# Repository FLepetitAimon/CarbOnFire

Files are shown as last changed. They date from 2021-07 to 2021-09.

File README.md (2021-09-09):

# Système CarbOnFire
***
## Contexte 
Le projet a été réalisé entre juin et aout 2021 au laboratoire d'aérologie de Toulouse, dans le cadre d'un stage de 4é année d'école d'ingénieur. La stage a été fait par François LEPETIT-AIMON et tutoré par Jean-François LEON. Si vous désirez des informations suplémentaires sur le projet, n'hésitez à contacter François LEPETIT-AIMON à l'adresse mail: francois.lepetitaimon@gmail.com

## Présentation du projet

ATTENTION : Avant d’utiliser le système, veillez à lire la fiche technique du projet.

CarbOnFire est un système de mesure d’émission de particules issues de la combustion de végétaux. Il s’inscrit dans un projet d’étude de l’exposition humaine aux particules fines issues de la combustion de biomasse et en particulier aux feux de forêt. Il est affilié au projet FIRECASTER de l’Agence National de la Recherche (ANR). Ce projet a pour but la création d'une plate-forme numérique de simulation des incendies de forêts et des panaches de fumée associées en zone méditerranéenne. Pour évaluer la quantité de fumée émise par un incendie, il est nécessaire de connaître les facteurs d'émission des polluants.  Les facteurs d’émission se définissent comme la masse d'un polluant spécifique émis dans l’atmosphère par kilogramme de végétation brûlée. Pour les évaluer, on mesure les rapports d'émission qui se définissent comme le rapport entre la masse de polluants émises sur celle des concentrations de CO et CO2. 

CarbOnFire est un système qui permet d’analyser la composition de fumées issues de combustions de végétaux. Le système est installé sur un sac à dos pour être facilement transportable.  Il est équipé d’un système de pompage qui aspire les fumées. L’aspiration se fait au bout d’un tuyau que l’utilisateur place au-dessus des feux. Le bout du tuyau est pourvu d’un filtre de quartz dont le rôle est de capter les particules. Après la mesure, le filtre est analysé au laboratoire par des méthodes chimiques, qui permettent de mettre en évidence sa composition. Les fumées filtrées qui arrivent du tuyau, circulent respectivement dans la pompe, le boîtier de mesure et enfin à travers le compteur à gaz. Elles sont ensuite rejetées dans l’air. Le cœur du système réside dans le boîtier de mesure. Il fait l’acquisition des concentrations de monoxyde (CO) et dioxyde de carbone (CO2), de la température et de la pression. Il enregistre les mesures dans une carte SD pour un traitement ultérieur, et transmet en direct, via Bluetooth, les mesures de gaz et de température. Celles-ci peuvent être visualisées sur le terrain avec un smartphone grâce à l’application CarbOnFire.

## Etat de fonctionnement du système

A l'issue des trois mois de développement, le premier prototype du système est en état de marche. Il fait l'acquisition des mesures de CO, CO2, température et pression. Il enregistre les données sur une carte SD et transmet les mesure de CO, CO2 et température vers une application android. L'ensemble du système est intégré sur un sac à dos. Les mesures réalisées en laboratoire et en conditions reélles ont permis de caractériser la qualité des mesures de gaz. Il en ressort qu la précision obtenue est insuffisante et qu'il faut l'améliorer. Le détail des mesures et de leur analyse est décrit dans la fiche technique du Projet.

## Contenu du Github

Le github contient les programmes arduino du projet, les documents techniques, le code de l'application android avec le fichier .apk, les fichiers des mesures réalisées, et enfin les fichiers associés à la conception du PCB.

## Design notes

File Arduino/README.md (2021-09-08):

# Codes Arduino
***

## Environement de Développement 

Pour écrire un programme et le téléverser sur la carte Arduino, vous pouvez utilisez l'IDE foruni par Arduino et téléchargeable gratuitementsur leur site internet (https://www.arduino.cc/en/software). Les codes sont écrit en C++. 

## Progamme Principale

Le fichier ProgrammePrincipale contient le code d'acquisition des mesures. Il effectue des mesures, les enregistre dans un fichier au format .CSV sur une carte SD et transmets trois d'entre elle via une communication bluetooth. Les trois grandeurs concernés sont la concentration de CO, la concentration de CO2 et la température. En complément du programme, il est recommandé d'utiliser l'application android CarbOnFire disponible sur le GitHub dans le répertoire CarbOnFrie_App.

Le montage electrique nécessaire au bon fonctionnement du programme est détaillé dans la fiche technique du projet (répertoire Documents_Techniques). 

## Programme RTC (Real-Time Clock)

Le programme RTC à pour but de régler la RTC. Il se peu qu'avec le temps, la RTC se décale de quelques minutes, ou que la pile soit vide. Dans ce cas, il est nécessaire de régler la RTC. Pour effectuer se réglage suivé les indicationsl suivantes:

1. Ouvrez, avec l'IDE Arduino, le programme test-rtc.ino disponible dans le repertoire Programe_RTC du Github
2. Branchez le shield SD-RTC sur une carte Arduino UNO, et branchez la carte à l'ordinateur. 
3. Téléverser le programme puis ouvrez le port série sur l'IDE
4. Réglez le baudrate du port série à 57600, la listes des commandes devrait s'afficher
5. Commencez par activer la RTC en tapant la commande **c 0 0** 
6. Puis renseignez l'heure actuelle avec la commande **tw yyyymmdd hhmmss dw** avec **dw** qui correspond au jour de la semaine (dim=1, lun=2, ..., sam=7)
7. Vérifiez le bonne mise à jour de l'heure en tapant la commande **tr**, l'heure actuelle doit s'afficher.
8. Reposisitionnez le Shield SD sur dans le boitier de mesure.

## Programme CN0396

Le programme CN0396Exemple sert lire la mesure de CO effectuée par la carte Analog Device CN0396 équpé d'un capteur de CO, CO-CX. La programme offre également la possibilité d'effectuer une correction en température. Le montage électrique est très simple, il suffit de monter la carte Analog Device sur une carte Arduino Uno et de téléverser le programme exemple. Si vous souhaitez utiliser la carte Analog avec un shield Sd, il vous faudra changer le pin CS du bus SPI d'une des deux cartes.

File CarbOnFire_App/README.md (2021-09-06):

# Application CarbOnFire
***
## Fonctionnalités

L'application CarbOnFire accompagne la prsie de mesure du système. Elle permet de visualiser en temps réel les valeurs de CO, de CO2, et de température mesurées par les capteurs. Elle utilise la connexion bluetooth du smartphone sur lequel elle est installée.

## Installation

L'insatllation de l'application se fait par le biais d'un fichier apk. De ce fait il est nécessaire d'avoir un appareil android, l'application ne sera pas instalable sur un appareil apple. Voci la liste des étapes à suivre:

1. Téléchargez sur votre ordinateur le fichier "CarbOnFire.apk" disponible dans le répertoire CarbOnFire_App du github.
2. Branchez votre smatrphone à votre ordinateur.
3. Autoriser le transfert des données par USB dans les paramètres de votre smartphone.
5. Via votre ordinateur, copiez le fichier .apk téléchargé précedement dans les fichiers de votre smartphone. 
6. Sur votre smartphone, lancer le fichier .apk  que vous venez de copier
7. Autoriser l'installation d'application de sources inconnues 
8. L'application devrait s'installer.

## Utilisation

Lorsque vous lancez l’application pour la première fois, il vous est demandé la permission d’accès à la localisation. Cette autorisation est nécessaire pour le fonctionnement du Bluetooth. Il vous faut l’accepter sinon l’application ne fonctionnera pas. Pour se connecter au boîtier, appuyez sur le bouton « DEVICE ». Une liste déroulante s’affiche avec les appareils Bluetooth détectés. Sélectionnez celui correspondant au boîtier. Par défaut, son nom est HMSOFT. Attendez que la connexion se fasse.
Dès que le système de mesure est connecté, les mesures s’affichent et se mettent à jour automatiquement.

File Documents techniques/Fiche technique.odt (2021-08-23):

Fiche Technique

Présentation

CarbOnFire est un système de mesure d’émission de particules issues de la combustion de végétaux. Il a été développé au laboratoire d’aérologie en août 2021. Ce document décrit l’architecture et la conception du système. Si vous désirez des informations supplémentaires sur le projet, n’hésitez pas à contacter François LEPETIT-AIMON à l’adresse électronique francois.lepetitaimon@gmail.com.

ATTENTION : Avant d’utiliser le système, veillez à lire la partie « indication d’utilisation »

Contexte du projet

CarbOnFire s’inscrit dans un projet d’étude de l’exposition humaine aux particules fines, et en particulier, aux émissions issues de feu de cuissons en plein air. Dans beaucoup de pays, la combustion de végétaux est utilisée comme outil de cuisine au quotidien. Le système permettra de calculer les facteurs d’émissions ainsi que les ratios de polluants par CO2 pendant la préparation d’un repas. Il mettra ainsi en évidence la nature de la combustion (complète ou incomplète), et le niveau de nocivité pour la santé du cuisinier. Des études ont déjà été menée et sont toujours menées actuellement. Par exemple en 2019, Aka Jacques Adon avait soutenu sa thèse sur l’impact sur la santé des aérosols issus de source urbaine en côte d’ivoire. Sa thèse est disponible à l’URL suivant : http://thesesups.ups-tlse.fr/4469/.

Caractéristiques techniques du système :

Tension d’alimentation | 12V
Précision mesure de CO | -+ 5ppm
Précision mesure de température | -+1°C
Précision mesure de pression | -+1hPa
Précision mesure de CO2 | -+50ppm
Débit d’air | 10l/min
Capacité carte SD | 32GB
Plage de mesure de température | -10°C à 50°C
Plage de mesure de CO | 0 à 2000ppm
Plage de mesure de CO2 | 0 à 5000ppm
Plage de mesure de pression
Dimensions | 60cm x 30cm x 30cm
Poids | 10Kg
Diamètre de filtre | 45mm

Conception globale du projet

CarbOnFire est un système qui permet d’analyser la composition de fumées issues de combustions de végétaux. Le système est installé sur un sac à dos pour être facilement transportable. Il est équipé d’un système de pompage qui aspire les fumées. L’aspiration se fait au bout d’une perche que l’utilisateur place au-dessus des feux. Le bout de la perche est pourvu d’un filtre de quartz dont le rôle est de capter toutes les particules. Après la mesure, le filtre est analysé au laboratoire par des méthodes chimiques, qui permettent de mettre en évidence sa composition. Les fumées filtrées qui arrivent de la perche circulent respectivement dans la pompe, le boîtier de mesure et enfin à travers le compteur à gaz, elles sont ensuite rejetées dans l’air. Le cœur du système réside dans le boîtier de mesure. Il fait l’acquisition des concentrations de monoxyde et dioxyde de carbone, de la température et de la pression. Il enregistre les mesures dans une carte SD pour un traitement ultérieur, et transmet en direct, via Bluetooth, les mesures de gaz et de température. Celles-ci peuvent être visualisées sur le terrain avec un smartphone grâce à l’application CarbOnFire.

Boîtier de Mesure

Le boîtier de mesure a pour rôle de caractériser quatre grandeurs physiques des fumées aspirées : la concentration de monoxyde de carbone, la concentration de dioxyde de carbone, la température et la pression.

Mesure du Monoxyde de carbone

Pour mesurer le monoxyde de Carbone, nous utilisons un capteur chimique. Le principe de mesure est voisin de celui d’une pile chimique. Le passage du gaz entre deux électrodes provoque une réaction d’oxydo-réduction. Cette réaction produit un courant entre les deux électrodes appelées Working Electrode et Counter Electrode. Dans la gamme de mesure, ce courant est proportionnel à la concentration de CO à laquelle est exposée le capteur. Un capteur chimique est caractérisé par sa sensibilité exprimée en courant par unité de concentration. Plus sa sensibilité est grande plus le courant circulant entre les électrodes sera important à concentration égale. En contrepartie la plage de mesure se restreint quand la sensibilité augmente.

Un des inconvénients de ce type de capteur est les sensibilités croisées. La géométrie du capteur et le choix du matériau des électrodes optimisent la sensibilité du capteur pour le gaz choisi, mais il subsiste des sensibilités non nulles pour d’autres gaz. Il est important de connaître ces gaz pour s’assurer que dans l’application prédestinée, il n’y ait pas de risque de les retrouver.

Pour notre application, nous avons besoin de mesurer des concentrations pouvant atteindre 2000ppm de monoxyde de Carbone. Nous avons choisi d’utiliser le capteur alphasense CO-CX dont la plage de mesure est 0-2000ppm. Sa sensibilité est comprise entre 55 et 100nA par ppm d’après le constructeur, ce qui représente un grand intervalle d’incertitude. Afin de réduire cette incertitude, il est nécessaire que le capteur soit étalonné avant son utilisation. Voici les principales caractéristiques assurées par le constructeur :

On peut retenir sur la qualité de la mesure que la réponse admet un bruit RMS de +-0,5ppm, que la mesure du 0 peut-être biaisée de -+3ppm et enfin que l’erreur de linéarité engendre au maximum une déviation de 40ppm par rapport à la valeur vraie.

Les principales sensibilités croisées sont les suivantes :

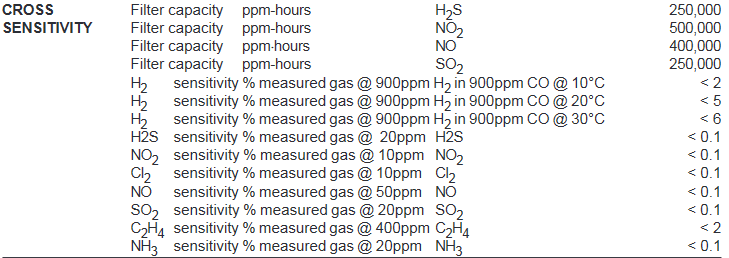
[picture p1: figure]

Il est important de noter que les performances du capteur sont impactées par la température. Plus la température est différente de 20°C, plus l’erreur de linéarité est grande et plus la dérive du zéro est importante. Voici les résultats de dérive en température fournis par le constructeur :

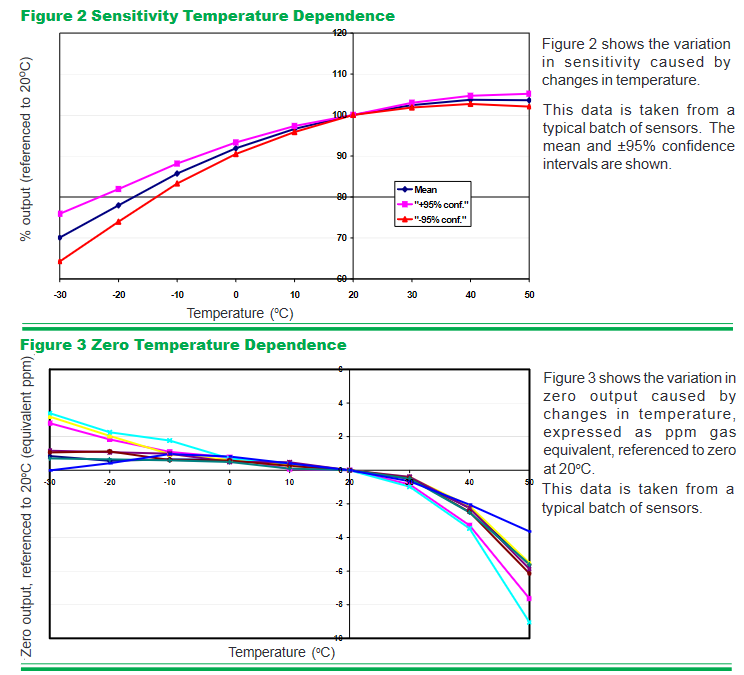
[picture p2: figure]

Pour pouvoir traiter la mesure, il faut amplifier le faible courant de réponse en un courant plus grand mesurable. Pour cela on utilise la carte électronique alphasense « 4 to 20 mA Digital Transmitter Board » qui est conçue spécialement pour le CO-CX. Elle amplifie le signal du capteur en un courant variant de 4mA à 20mA. Cette amplification se fait grâce à un circuit potentiostatique dont voici le schéma du montage :

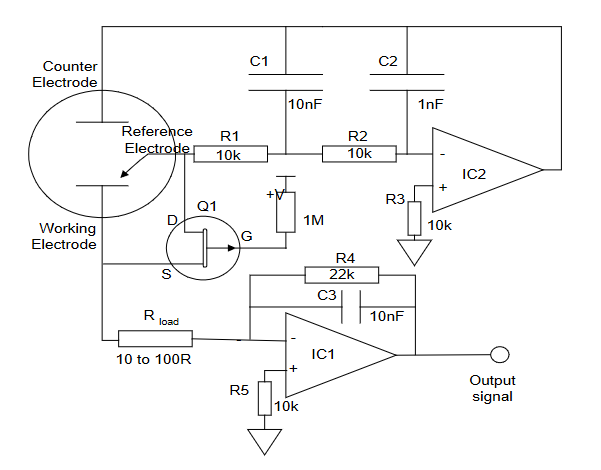
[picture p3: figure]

On peut noter que le capteur possède une 3ème électrode « Reference Electrode ». Cette électrode sert à appliquer une tension d’offset entre elle et la « Working Electrode ». La valeur de cette tension dépend du capteur utilisé, pour le capteur CO-CX, elle doit être nulle.

La sortie de la carte électronique alphasense est un courant variant de 4mA à 20mA. Ce courant de sortie est numérique avec une résolution de 0.75µA. Rapporté à l’entrée cela correspond à une résolution de 11nA. On sait que la sensibilité du capteur est comprise entre 55 et 100 nA/ppm et que son bruit RMS est de l’ordre de 0.5ppm. En termes de courant, ce bruit vaut entre 27nA et 50nA. La résolution de la carte est inférieure à ce bruit, donc elle ne sera pas limitante.

En sortie, la précision de la carte est de -+5µA, a laquelle il faut ajouter le bruit RMS pouvant aller jusqu’à 2 µA. Rapporté à l’entrée l’incertitude sur la mesure est d’environ 100nA. Cette incertitude est limitante car elle est supérieure au bruit du capteur. En termes de concentration, cela correspond à une incertitude de -+1 à 2ppm. Il faut encore ajouter à cette erreur la dérive en température qui est importante : -+0.2uA/°C en sortie. On arrive à -+4ppm de précision à 25°C, soit 10 fois moins précis que la précision potentielle du capteur seul.

La carte est alimentée en 10-30V par un connecteur molex KK2,54 de 2 pins. La valeur du courant en sortie de la carte est convertie en tension en ajoutant une résistance en série entre l’alimentation et le capteur :

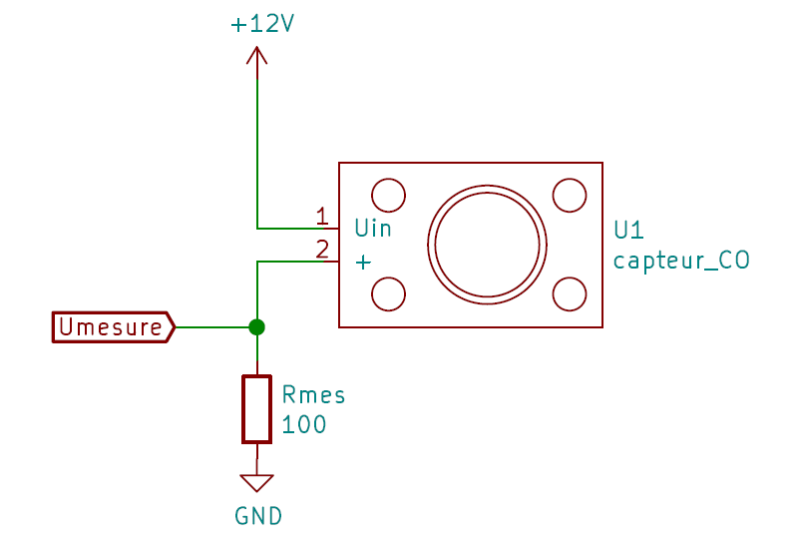
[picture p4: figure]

En utilisant la loi d’ohm on obtient les plages de tensions de mesures suivantes :

U0ppm = 0,004Rmes ; U1000ppm = 0,020Rmes.

La résistance de mesure induit une chute de tension aux bornes du capteur par rapport à la tension d’alimentation. La valeur maximale de cette chute de tension est de 0,020R. Malgré cette chute, la tension aux bornes du capteur ne doit pas être inférieure à 10 volts. La chute de tension doit donc être inférieure à une tension seuil :

dUseuil= Ualimentation – 10V

Dans notre cas, la tension d’alimentation vaut 12V, donc la chute de tension doit être inférieure à 2V. En terme résistif, la résistance de mesure doit être inférieure à une résistance seuil :

Rseuil = dUseuil/Imax = 2/0,02 = 100Ohms.

Nous avons choisi Rmes = Rseuil = 100Ohms pour maximiser la plage de tensions de mesures et ainsi optimiser la résolution numérique de l’adc.

N.B : Si vous souhaitez obtenir d’avantage d’informations sur le capteur et sa carte électronique alphansense, les datasheets et les notices d’utilisations sont disponibles en annexe.

Test et étalonnage

Nous avons mesuré la réponse du système pour deux concentrations de CO connues, une concentration de 0ppm et une concentration de 92ppm. Les mesures ont été réalisées pendant une période de forte chaleur, la température à l’intérieur du boitier a atteint 40°C. Cette température peut impacter à -+5ppm les résultats présentés.

Pour la concentration de 0ppm, la concentration initiale dans l’air ambiant de la salle de mesure est de 15ppm. L’air injecté dans le boitier a une concentration en CO de 1bpm, bien inférieure au bruit du capteur -+0.5ppm. Voici les résultats obtenus pour un débit d’air de 1l/min :

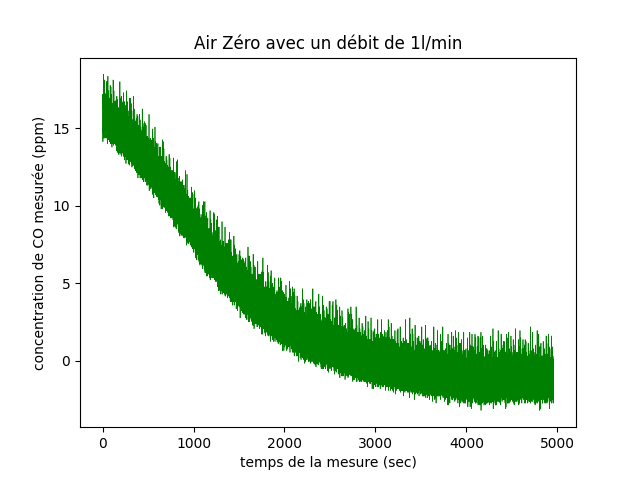
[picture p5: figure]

La mesure du zéro se stabilise légèrement en-dessous de 0ppm, à environ -2ppm. Cela peut venir de plusieurs paramètres : la dérive en température ou le mauvais étalonnage du capteur. On peut remarquer que le bruit de mesure est de -+3ppm. Cela correspond aux spécifications attendues qui sont de -+3ppm.

Le temps de réponse du capteur est très long, on doit attendre entre 30 minutes et 1 heure pour obtenir un zéro stable. Le constructeur ne s’est pas avancé sur le temps de réponse à 0ppm, mais ce temps de réponse est du même ordre de grandeur que celui du capteur de CO2. La géométrie du système et en particulier à l’écartement du capteur par rapport au flux d’air peut également augmenter le temps de réponse.

La deuxième concentration étudiée est le 92ppm. La concentration initiale dans le boitier est de -2ppm. L’air est injecté dans le boitier avec un débit de 9.7l/min. Voici les résultats obtenus :

La précision de la mesure est du même ordre de grandeur que pour le 0ppm, à savoir -+ 5ppm. Le temps de réponse est de 50 secondes alors que le constructeur annonçait un temps de réponse de 40 secondes pour une variation de 0ppm à 400ppm. Nous sommes au-dessus de ce temps de réponse, les hypothèses sur les raisons de ces écarts sont les mêmes que pour le 0ppm, à savoir l’éloignement du capteur par rapport au flux d’air.

En résumé, la précision des résultats obtenues correspond à la précision attendue compte tenu des caractéristiques du capteur et de la carte de traitement du signal. La mesure est précise à -+5ppm avec un bruit de mesure de -+5ppm. Le temps de réponse est plus important mais reste dans l’ordre de grandeur annoncé par le constructeur.

Alternatives

La carte électronique Alphasense limite la sensibilité du capteur. Elle admet un bruit de mesure bien supérieur au bruit généré par le capteur chimique. D’autres alternatives existent, par exemple la carte EVAL-CN0396-ARDZ développée par Analog Device, semble avoir une réponse plus stable.

Voici la comparaison des réponses des deux cartes de mesures équipées du même capteur CO-CX:

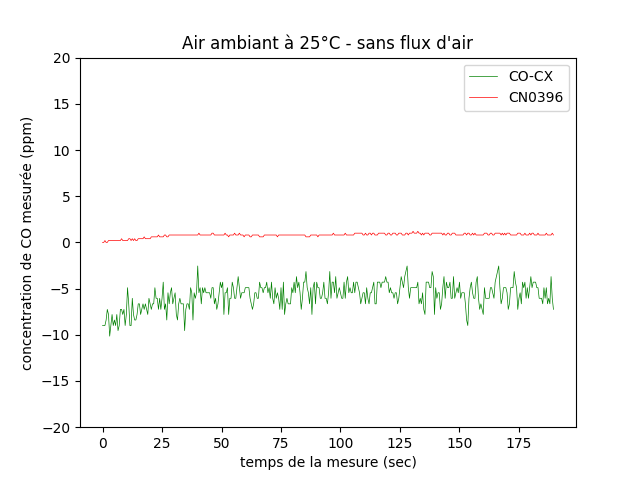
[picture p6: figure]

On voit clairement que la carte CN0396 fournie une réponse beaucoup plus stable (-+0.05ppm). Pour conclure sur la précision de la carte, il faudrait effectuer des tests à concentration connues comme présentés précédemment. Malgré tout, on peut faire l’hypothèse que la concentration de CO en intérieure est très proche de 0ppm. Dans le cadre de cette hypothèse, la précision de la carte Analog Device semble très bonne (-+0.2ppm).

En revanche en termes d’intégration dans un système de mesure, la carte CN0396 est plus contraignante. Elle s’utilise uniquement avec une carte arduino uno. Elle est montée en shield, ce qui oblige à prendre un boitier suffisamment haut et limite les choix de placement du capteur. Une possibilité serait d’imprimé un PCB personnalisé avec le circuit électrique de la carte CN0396. Voici le schéma électrique :

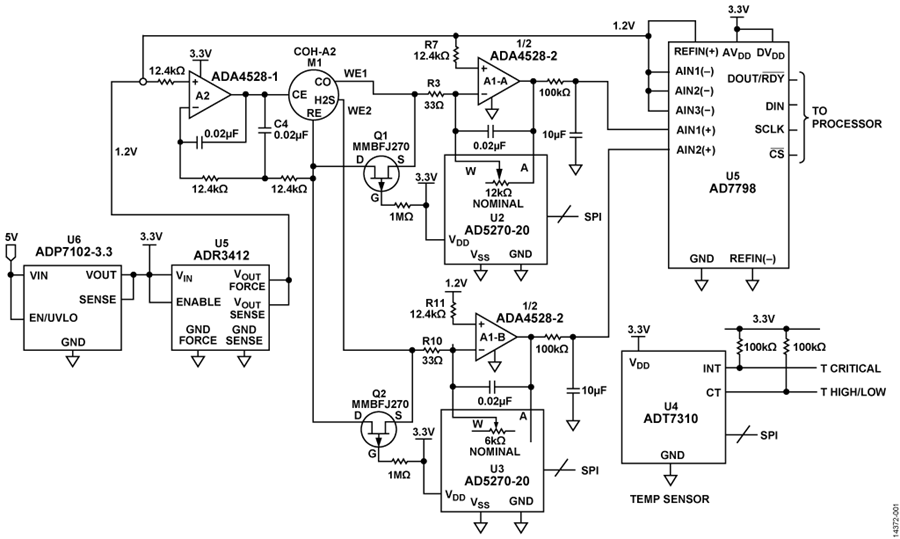
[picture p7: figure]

Mesure du Dioxyde de Carbone

La mesure de monoxyde de Carbone est assurée par un capteur infra-rouge NDIR Alphasense. Voici le principe de fonctionnement. Une LED infra-rouge envoie des pulses de courant à travers une cavité, qui communique avec l’air ambiant. Deux photodétecteurs sont installés à l’intérieur de la cavité face à la photodiode. Le premier est dit actif et le second est dit de référence. Ils mesurent l’intensité lumineuse transmise à travers la cavité. Le photodétecteur actif est équipé d’un filtre qui transmet uniquement la longueur d’onde d’une raie d’absorption du CO2, (lambda = 4µm). De cette manière lorsque la concentration en CO2 augmente dans la cavité, l’intensité lumineuse transmise diminue. L’autre photodétecteur est équipé d’un filtre qui absorbe uniquement la longueur d’onde de la raie d’absorption. De cette manière l’intensité lumineuse transmise n’est pas impactée par la variation de concentration de CO2. La cavité de référence sert à compenser les variations d’intensité d’émission lumineuse.

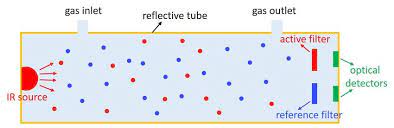
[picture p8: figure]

La concentration de CO2 dans l’air ambiant est fonction de la différence des mesures d’intensité lumineuse entre les deux détecteurs. Les photodétecteurs sont sensibles aux variations de température, c’est la raison pour laquelle ils sont accompagnés d’une thermistance permettant d’établir une correction de compensation thermique sur la mesure.

Pour notre application nous utilisons le capteur Alphasense IRC-A1 de type IAQ dont la plage de mesure est 0-5000ppm. Sa résolution est de -+1ppm à 0ppm et peut atteindre -+15ppm à 5000ppm. La précision du capteur est de -+50ppm (en utilisant les coefficients universels de linéarisation, annexe AAN401-05). Le temps de réponse du capteur est inférieur à 40 secondes d’après le constructeur. En revanche pour atteindre le zéro les temps de réponse sont plus long. Il faut 30 secondes pour atteindre le 0 à -+100ppm et il faut 30 minutes pour atteindre un zéro qui respect les spécifications constructeurs à savoir -+1ppm.

Voici les performances générales du capteur :

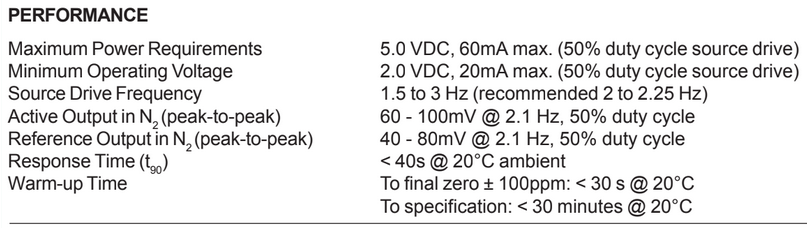
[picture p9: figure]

Voici le descriptif des broches du capteur indiqué dans la datasheet :

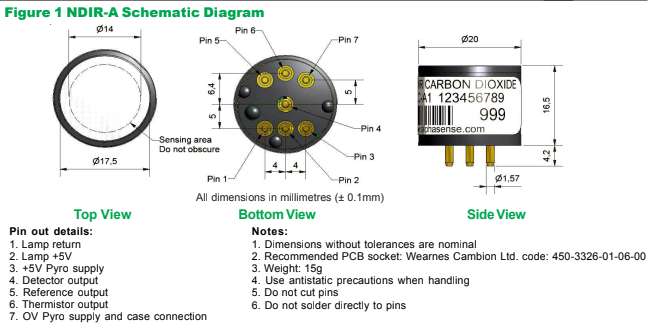
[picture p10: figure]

Le signal d’alimentation de la source lumineuse doit être un signal carré de 2 à 2,5Hz de fréquence, de rapport cyclique 50 % et d’amplitude 5V. La source de tension doit avoir une impédance de sortie d’environ 9 à 10Ohms et doit pouvoir fournir un courant de 50 à 60mA. Pour créer ce signal, on peut utiliser un transistor MOSFET à canal n couplé à un signal carré sur la grille (voir figure 2 pour le branchement). Cependant il faut bien s’assurer que le GND du transistor et le GND des photodétecteurs soit isolés pour éviter toutes perturbations de la mesure.

Les signaux bruts issus des photodétecteurs sont composés d’un offset d’environ 0,7 à 1V et d’une composante alternative de fréquence identique à la fréquence d’alimentation de la source lumineuse. Cette oscillation a une amplitude de 20mV à 50mV peak-to-peak qui varie en fonction de la transmission lumineuse à l’intérieur de la cavité. Pour traiter le signal il faut filtrer la composante continue ainsi que les hautes fréquences puis amplifié le signal :

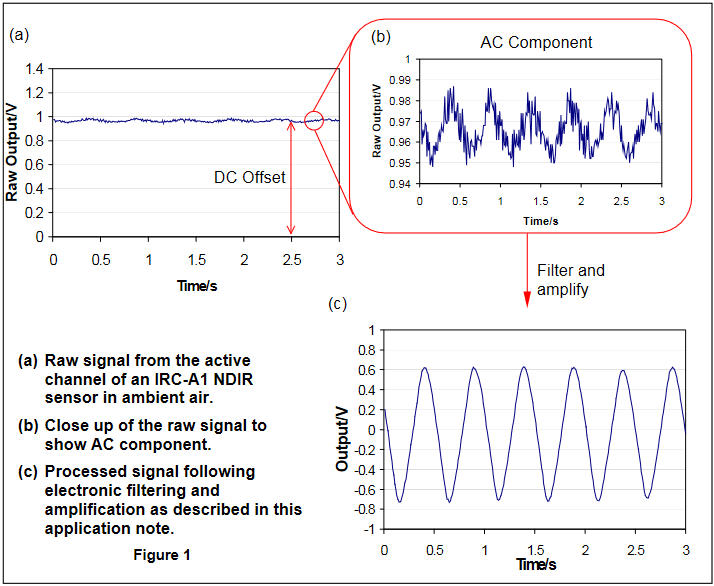
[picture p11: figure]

On obtient un signal sinusoïdal pour chacune des deux photodiodes, dont l’amplitude traduit le taux de transmission des rayons issus de la LED infra-rouge à travers la cavité.

Voici un schéma électrique qui permet de faire clignoter la source lumineuse et amplifier le signal des photodétecteurs :

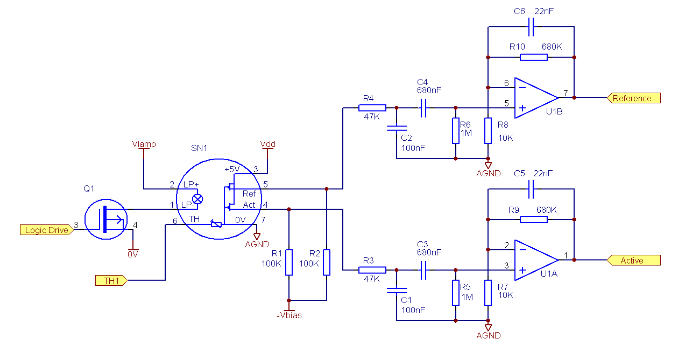
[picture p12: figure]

L’annexe AAN 202-04 détail la conception du circuit.

La thermistance à coefficient de température négatif (NTC), servant à mesurer la température, vaut 3000Ohms à 25°C et son coefficient B vaut 3450 K. On peut évaluer la valeur de la résistance en fonction de la température grâce à la relation de Steinhart-Hart simplifiée valable sur la plage de température de fonctionnent du capteur :

R(T)= R0 * exp(B*(1/T - 1/T0))

avec T0 = 25°C et R0 = 3000Ohms

En travaillant l’équation on obtient la valeur de la température en fonction de la résistance mesure :

T = T0*B/(T0*ln(R(T)/R0)+B)

Dans le capteur, la thermistance est connectée entre les broches 6 et 7. Pour effectuer la mesure de résistance, il faut connecter la broche 6 du capteur en série avec une résistance de valeur connue, et une source de tension également connue. En utilisant le principe du pont diviseur de tension, on peut connaître la valeur de la thermistance et donc mesurer la température :

Ainsi R(T) = (Vcc/Umes)*R1 – R1

Les détails des calculs de concentration de CO2 et de compensation thermique sont disponibles en annexe (document AAN 201-06).

Dans notre cas nous avons utilisé la carte alphasense IRC-TX spécialement conçue pour le capteur IRC-A1. Elle renvoie un signal en courant variant de 4mA à 20mA. La précision de la mesure est la même que celle du capteur, à savoir -+50ppm.

La carte est alimentée en 12-30V par les pins 1 et 2 du connecteur molex KK2,54 4-pins. Le principe de l’acquisition est le même que pour le capteur de CO. Un courant proportionnel à la concentration de CO2 allant de 4mA à 20mA circule entre le pin 3 et le pin 4 du connecteur molex. Une résistance de mesure est intégrée en série entre les pins 3 et 4 pour convertir la réponse en courant en une réponse en tension. La tension maximale mesurable par notre système d’acquisition est de 5V. D’après la loi d’Ohm, une tension maximale de 5V pour un courant maximal de 20mA est obtenue pour une résistance Rmesure = Umax/Imax = 250Ohms. La valeur standard la plus proche est 220Ohms, c’est celle que nous utilisons.

En résumé, on obtient en entrée de notre système d’acquisition une tension proportionnelle à la concentration de CO2 variant de Umin = 0.004R = 0,88V à Umax = 0.020R = 4,4V, sur la plage de mesure 0-5000ppm.

Voici le branchement électrique de la carte IRC-TX :

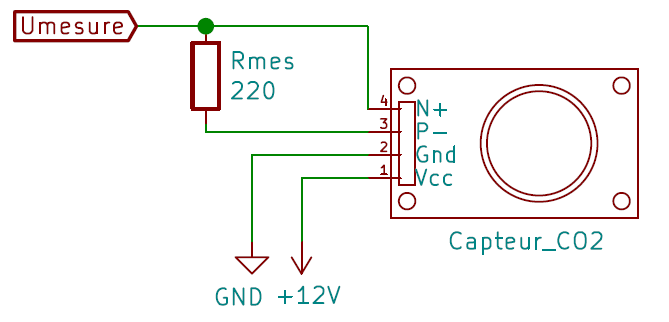
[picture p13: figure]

Tests et résultats

Comme pour le capteur de CO, nous avons étudiés la réponse la carte IRC-TX couplée avec le capteur IRC-A1 pour deux concentrations de CO2 : 0ppm et 1000ppm.

Pour le 0ppm, nous utilisons une bombonne qui fixe le CO2 de l’air ambiant. La concentration ainsi obtenue, est en toute vraisemblance inférieure à 1ppm, mais nous n’avions pas d’appareils de mesure permettant de le vérifier au moment de l’expérience. Nous en ferons donc l’hypothèse. Voici les mesures observées :

On peut observer que la mesure se stabilise à 0ppm -+10ppm. Le temps de mesure est d’environ 40 minutes. Le constructeur assurait une précision de -+50ppm et un temps de réponse de 30minutes. La précision mesurée est en accord avec les spécifications du constructeur, en revanche le temps de réponse est un peu plus long. Ce délai est sans doute dû à la géométrie du système, comme nous en avons discuté pour le capteur de CO.

La mesure de 1000ppm est faite avec une bouteille pressurisée de concentration 998ppm -+0,1 %. Elle est branchée directement sur le boîtier, le débit est réglé à 10 l/min. Voici la courbe obtenue :

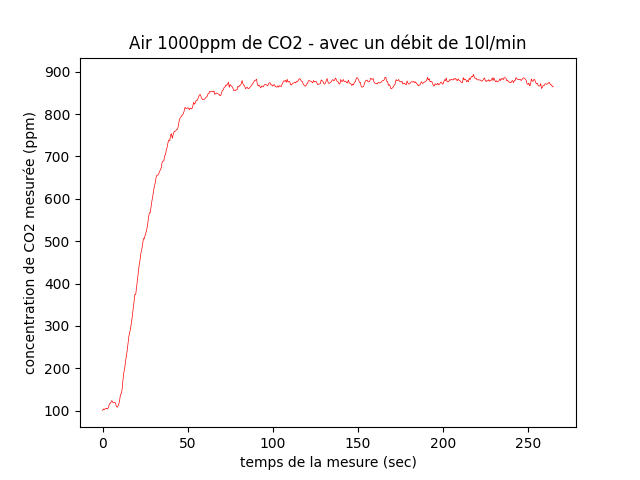
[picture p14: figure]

On peut observer que la valeur de stabilisation est de 900 ppm -+10ppm soit un écart de 100ppm par rapport à la concentration réelle. Cet écart est en dehors des marges du constructeur, et n’est pas acceptable. Il faudrait effectuer un étalonnage du capteur pour corriger cette imprécision. Le document d’assistance à l’étalonnage des capteurs, est fourni par alphasense et est disponible en annexe.

Le temps de réponse est d’environ 40 secondes. Il est légèrement supérieur aux 30 secondes prédites par le constructeur. Une fois encore cet écart peut être dû à la géométrie du système. Dans le cadre de l’application ce temps de réponse est acceptable, c’est la raison pour laquelle nous n’avons pas mis en œuvre des solutions pour le réduire.

Mesure de température et de pression.

Les mesures de température et de pression sont obtenues avec le capteur BMP280. C’est un capteur qui communique via le bus i2c. Il mesure la température ambiante avec une précision de 1°C et la pression ambiante avec une précision de 1hPa. À partir de la mesure de pression atmosphérique, le BMP280 peut calculer l’altitude à 1 mètre prêt. Cette précision est atteinte à la condition de renseigner quotidiennement la pression courante à l’altitude 0, qui varie en fonction des conditions météorologiques.

L’alimentation du capteur se fait par les pins 1 et 2 du connecteur Grove. Les mesures sont communiquées par les canaux SCL et SDA du bus i2c (pin 3 et 4 du connecteur Grove).

Système d’acquisition des mesures de gaz.

L’acquisition des mesures est assurée par l’Arduino Uno rev3 assisté d’un ADC 16-bits adafruit. Nous avons fait le choix d’ajouter un ADC extérieur en raison des mauvais résultats obtenus en utilisant l’ADC de l’Arduino. En termes de résolution théorique, l’ADC 10-bits de l’Arduino aurait suffi pour obtenir une précision de 6ppm sur la mesure de CO et de CO2. Cependant en comparant les résultats obtenus avec l’Arduino et avec l’ADC Adafruit, on observe une nette différence de mesure, supérieure à la résolution théorique mesure (-60ppm par rapport à l’adc de l’arduino). Malgré sa résolution suffisante, l’Arduino n’a pas la précision nécessaire. L’ADC utilisé est un ADS1115 Adafruit 16-bits. Il peut accueillir 4 canaux analogiques et communique en i2c en utilisant la librairie ‘Adafruit_ADS1X15.h’.

Ainsi toutes les acquisitions de mesures (température, pression, concentrations de gaz) se font avec les canaux i2c de l’Arduino.

Enregistrement des mesures et RTC.

La carte arduino est accompagnée d’un shield SD de TRU COMPONENT muni d’une Real Time Clock (RTC) (Ref : TC-8579880). Il équipé d’un lecteur de carte SD et d’une RTC DS1307ZN. La RTC est alimentée par une pile bouton de type CR1220, qui permet de garder en mémoire la date et l’heure, quand le système est éteint.

Communication Bluetooth

CarbOnFire est équipé d’un module Bluetooth qui communique par bus série v.3. Le module est branché avec un connecteur Grove dont les pins correspondent dans l’ordre au tx, rx, Vcc, Gnd. Les pins digitaux 0 et 1 de l’arduino sont par default dédiés à la communication série, le branchement du module est donc très simple :

Panneau Face avant

Sur la face avant du boîtier, on retrouve les éléments de contrôle d’alimentation :

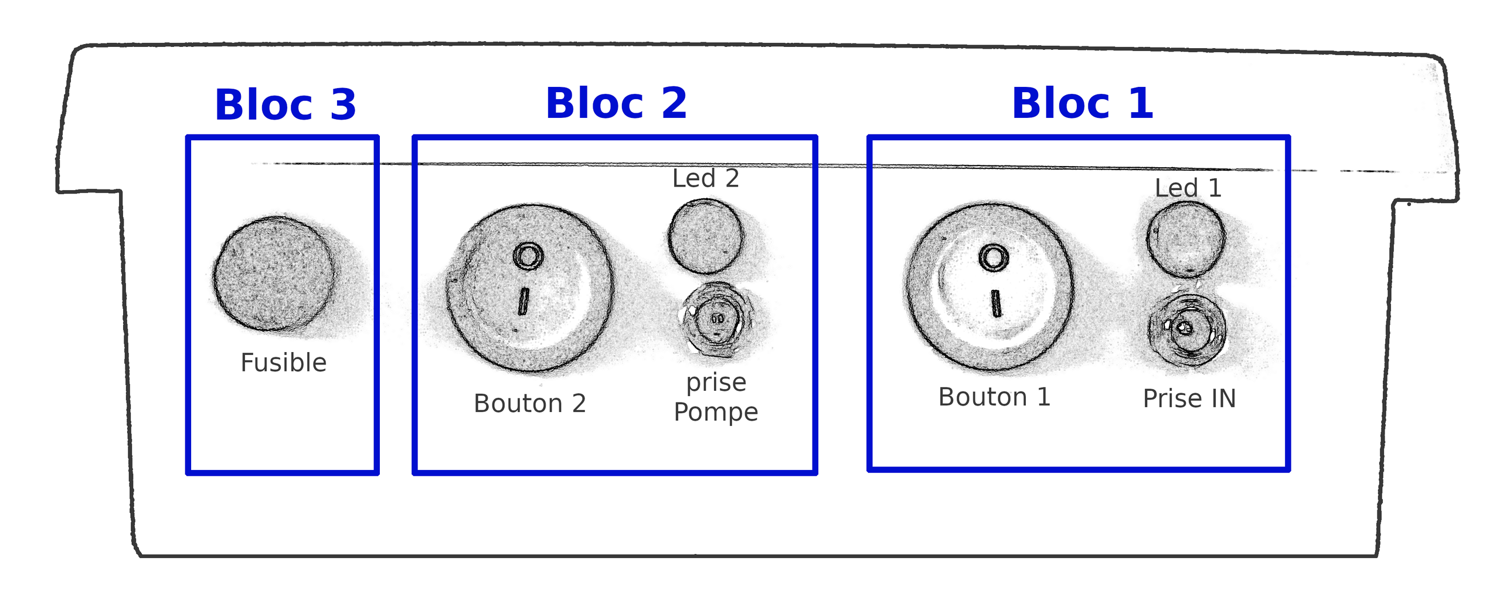
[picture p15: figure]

Le bloc 1 sert à alimenter le système de mesure. Il est constitué d’un bouton ON/OFF, d’une prise d’alimentation CC 12Volt et d’un voyant vert. Le voyant s’allume lorsque le système de mesure est en marche.

Le bloc 2 sert à alimenter la pompe. Il est constitué des mêmes éléments que le bloc 1, à savoir un bouton, un voyant et une prise CC. Il est important de noter que la prise CC du bloc 2 est une sortie d’alimentation contrairement à celle du bloc 1 qui est une entrée. Elle est connectée aux bornes de la pompe avec un câble CC vers double cosses.

Le bloc 3 est constitué d’un porte-fusible qui protège le système de mesure d’une éventuelle surcharge. Il accueille un fusible de 500mA changeable facilement depuis l’extérieur.

Isolation de l’alimentation de la pompe

Pour assurer une bonne précision dans les mesures, l’alimentation des capteurs doit être stable. La batterie fournie une tension très stable, mais dans la mesure où la pompe est branchée en parallèle du système de mesure, elle peut induire un bruit dans la tension d’alimentation. Pour éviter ce bruit, nous avons ajouté deux éléments. Le premier est une diode de roue libre. Elle empêche la propagation d’un courant inverse dû à l’inertie du rotor lors de l’arrêt de la pompe. Le deuxième est un condensateur de filtrage de 1uF, qui filtre les variations de tensions à haute et moyenne fréquence dû à la rotation du moteur.

Organisation des éléments dans le boîtier et assemblage mécanique

Le boîtier est organisé en deux parties délimitées par une cloison en PVC horizontale. La partie inférieure est un SAS dans lequel circule le flux d’air. Les capteurs de gaz et le BMP280 sont situés dans ce SAS pour baigner dans l’air extérieur. Les deux embouts du conduit d’air sont placés face à face, et les capteurs de gaz sont légèrement décalés par rapport au flux d’air.

La partie supérieure du boîtier accueille le montage électrique. On y retrouve les cartes des capteurs, le Shield SD monté sur la carte Arduino Uno, le module Bluetooth, l’ADC, le bornier, les connections du panneau de face avant, ainsi que tous les câbles de connexions entre chacun des ces éléments.

Les boutons de contrôle sont encastrés dans la paroi du boîtier, tandis ce que les voyants, les prises d’alimentation et le porte-fusible sont serrés à la paroi avec un écrou. Les deux embouts traversent-cloisons d’entrée et de sortie d’air, sont également serrés sur la paroi avec un écrou. Le reste des composants sont fixés sur la cloison de séparation par un système de vis écrous.

Étanchéité du boîtier

Les jonctions du panneau de face avant et des embouts traversent-cloisons sont susceptibles de générer des fuites. Pour éviter ce problème, ces zones sont étanchéifiées par le dépôt de silicone liquide. En séchant elle durcit et forme un couche souple et étanche. Le couvercle du boîtier est équipé d’un joint, qui assure l’étanchéité quand le boîtier est fermé.

Impact du débit sur les mesures

Une des options pour améliorer le temps de réponse des mesures de gaz, est de placer les capteurs dans le flux d’air. Si cette option est appliquée, il faut prendre en compte l’impact de la vitesse du flux d’air sur les mesures. En effet il semblerai que la vitesse du flux d’air ait une forte influence sur la mesure de CO2 et une légère influence sur la mesure de CO.

Pour effectuer cette observation, nous avons fait une série de mesure dans l’air ambiant avec la pompe éteinte et avec la pompe allumée. Voici les résultats obtenus :

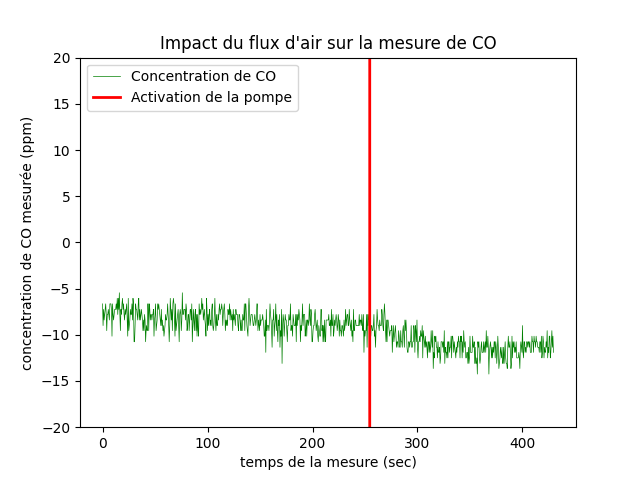
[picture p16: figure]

On observe que la mesure de CO décroît de 5ppm lorsque la pompe se met en route, alors que la mesure de CO2 augmente de 50ppm. Pour le CO ces variations semblent acceptables. Il faudrait vérifier que le phénomène ne s’amplifie pas pour des concentrations de CO plus élevée.

La variation de la mesure de CO2 est à la limite de l’acceptable, il faudrait étudier ce phénomène de manière plus rigoureuse de manière à corriger la dérive de la mesure.

Batterie

Le système est alimenté en 12V avec une batterie de Plomb rechargeable de 7 A.h. Les batteries utilisées sont de la marque Radio Spare, réf : 537-5488. Chaque système est équipé d’une unique batterie qui alimente la pompe et le boîtier de mesure. L’autonomie du système est d’environ 7heures.

Une autre solution serait d’alimenter la pompe avec une autre batterie pour réduire l’impact de l’alimentation de la pompe sur l’alimentation du système de mesure.

Programme Arduino

Comme tous les programmes arduino, le script se décompose en deux parties : une partie setup() qui s’exécute une unique fois à la mise sous tension, et une partie loop() qui tourne en boucle. Voici les étapes qu’exécute le programme :

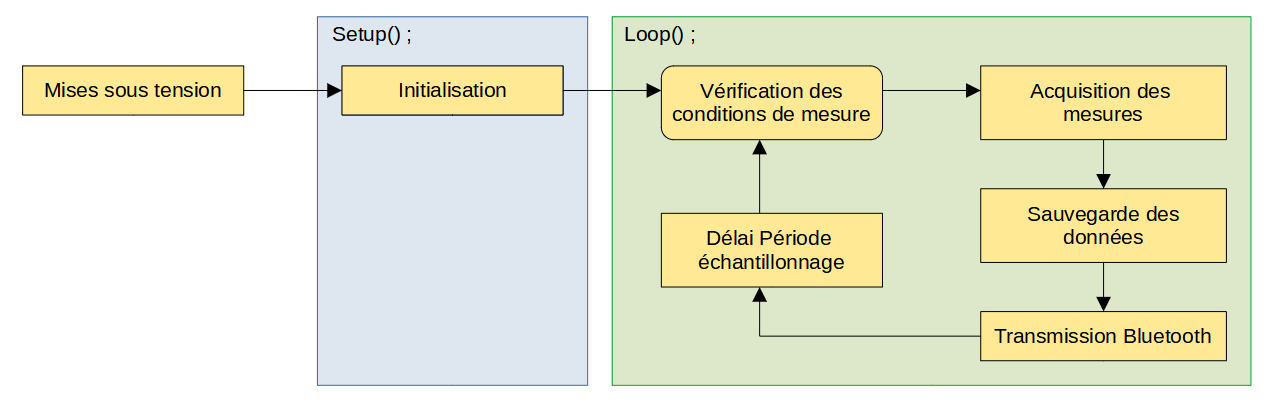
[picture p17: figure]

Initialisation

Dans le setup(), nous préparons les composants électriques pour qu’ils soient opérationnels. De manière générale chaque composant à une librairie dédiée dans laquelle figure une fonction d’initialisation intitulée classiquement begin(). Elle permet de vérifier que la communication se fait entre la carte et le composant (branchement, temps de réponse, …) et parfois de définir des paramètres (ex : baudrate pour le Serial). Dans notre cas il y a 4 éléments à initialiser : le bmp280, le shield SD, l’adc 16-bits et le port série du module Bluetooth.

Plus loin dans le programme, les données sont écrites dans un fichier sur la carte SD. C’est un fichier au format csv (Coma Separate Values), avec une première ligne d’entête correspondant aux intitulés des colonnes de mesure :

Si le fichier de mesure sur la carte a été supprimé, où s’il n’a jamais été créé, il faut le créer et y écrire la première ligne d’entête. Cela se fait dans la partie Setup(). Un répertoire « donnée » est d’abord créé, puis un fichier DATA y est ajouté avec la première ligne d’entête. A l’inverse, si le fichier existe déjà et qu’il contient des mesures, il ne faut ni les effacer, ni ajouter une ligne d’entête en plein milieu. Les nouvelles mesures seront ajoutées à la suite de celles déjà écrites.

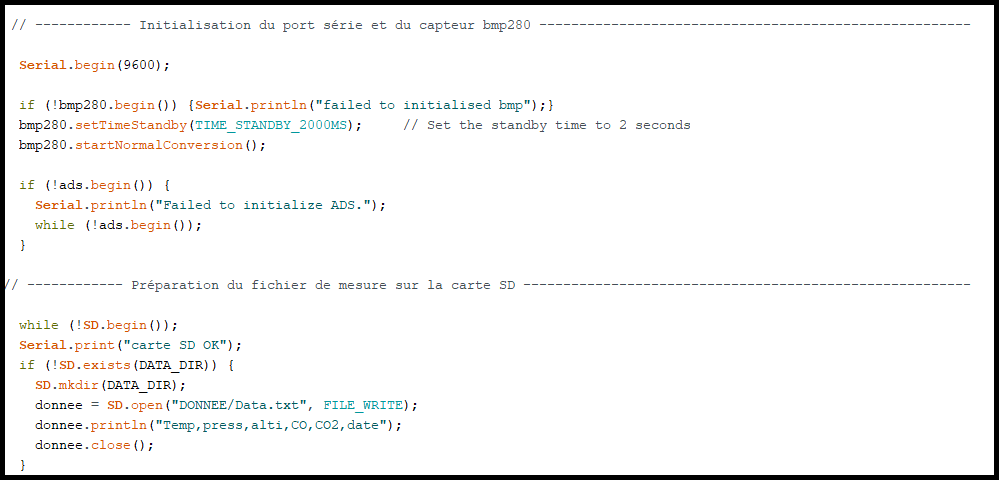
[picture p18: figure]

Vérification des conditions de mesures

Une fois l’initialisation faite, nous entrons dans la boucle du programme. C’est dans cette boucle que s’effectue les mesures et leur gestion, notamment leur sauvegarde. Avant de démarrer une acquisition, il faut vérifier que nous sommes en capacité d’enregistrer la mesure. Autrement dit, il faut s’assurer qu’il y ait une carte SD dans le lecteur et que la communication avec le Shield SD puisse s’établir. Le programme contient une boucle bloquante qui attend qu’une carte SD soit insérée dans le lecteur.

Acquisition des mesures

L’acquisition des mesures de CO et CO2 se fait grâce à l’adc 16-bits qui communique en I2C. La fonction readADC_singleEnded(Pin) renvoie une valeur numérique entre 0 et 655536. Celle-ci est proportionnelle à la tension mesurée sur le broche numérotée « Pin ». La valeur 0 correspond à une tension de -Vsat et la valeur 655536 correspond à une de tension de +Vsat. L’ADC possède un gain réglable allant de x2/3 (par défaut) jusqu’à x16. La tension Vsat dépend de ce gain :

GAIN | Vsat | Résolution
x 2/3 | 6.144 V | 0.1875 mV
x 1 | 4.096 V | 0.125 mV
x 2 | 2.048 V | 0.0625 mV
x 4 | 1.024 V | 0.03125 mV
x 8 | 0.512 V | 0.015625 mV
x 16 | 0.256 V | 0.0078125 mV

Pour convertir la valeur binaire en une tension de mesure, on utilise la fonction computVolts(valeur_binaire). Elle renvoie la tension en tenant compte du GAIN sélectionné.

Le programme Arduino contient deux fonctions, ConcentrationCO() et ConcentrationCO2(), qui renvoient respectivement la mesure de concentration de CO et de CO2. Elles utilisent le principe de mesure décrit plus haut dans les parties « mesure de CO2 » et « mesure de CO ». Dans un premier temps, la tension mesurée par l’adc aux bornes des résistances de mesure est convertie en courant par loi d’ohms.

Imes = Umes/Rmes

Sachant qu’un courant de mesure de 4mA équivaut à une concentration de 0ppm et qu’un courant de mesure de 20mA équivaut à une concentration de 5000ppm, on déduit la relation suivante :

Cmes = (Imes – I0ppm) * (5000ppm/I5000ppm)

Au final on a:

Cmes = ((Umes/Rmes) – I0ppm) * (5000ppm/I5000ppm)

Les mesures de CO, CO2, température, pression et altitude ainsi que la date sont enregistrées temporairement dans un tableau de float intitulé Tab_Mesure[]

Sauvegarde sur la carte SD

La nouvelle série de données disponible dans le tableau de mesure est ajoutée au fichier de mesure sur la carte SD par l’appelle de la fonction EcritureCarteSD(). Les données sont écrites selon les règles de syntaxe du format CSV : les mesures sont séparées par des virgules, et chaque série de mesure se finit par un retour à la ligne.

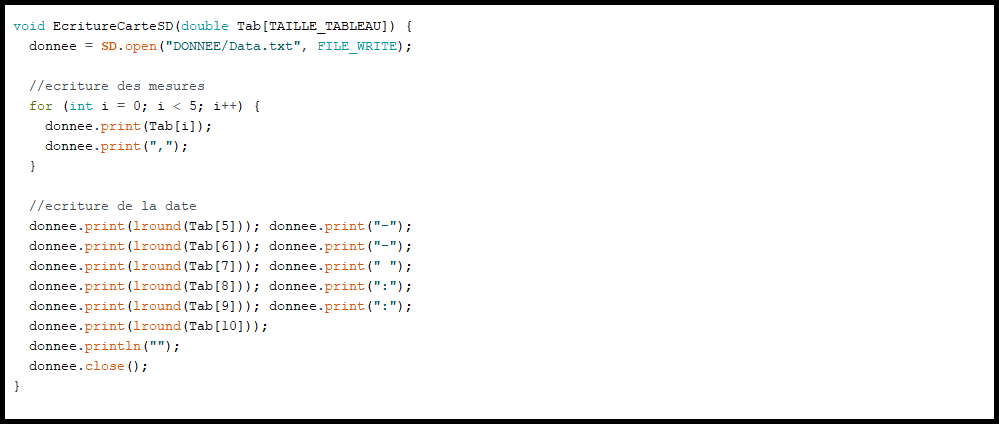
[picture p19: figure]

Transmission Bluetooth

La transmission Bluetooth se fait grâce au module Bluetooth qui utilise le port série (pin rx et tx). Uniquement trois données sont transmises par Bluetooth, à savoir la température, la concentration de CO et la concentration de CO2. Elles sont envoyées dans une trame de caractères dont la syntaxe est bien définie : chaque série de mesure se fini par une virgule et dans une même série, chaque mesure est séparée par un point-virgule.

Délai période d’échantillonnage

En fin de boucle, est placée une temporisation de T secondes, avec T la période d’échantillonnage souhaitée. Elle est fixée à 1 secondes. Il est possible de la diminuer, mais dans la mesure ou les changements de concentrations se font de manière progressive et lente (de l’ordre de quelques secondes), et sachant que le temps de réponse des capteurs est de 30 secondes, nous n’avons pas trouvé nécessaire de prendre plus de mesures.

Application Android

Fonctionnement de l’application

L’application Android permet de visualiser en direct les mesures de CO, CO2 et de température mesurées par le boîtier. Au lancement de l’application, nous observons l’interface d’accueil dont la partie supérieure permet de gérer l’état de connexion avec le système, tandis ce que la partie inférieure permet d’afficher les mesures.

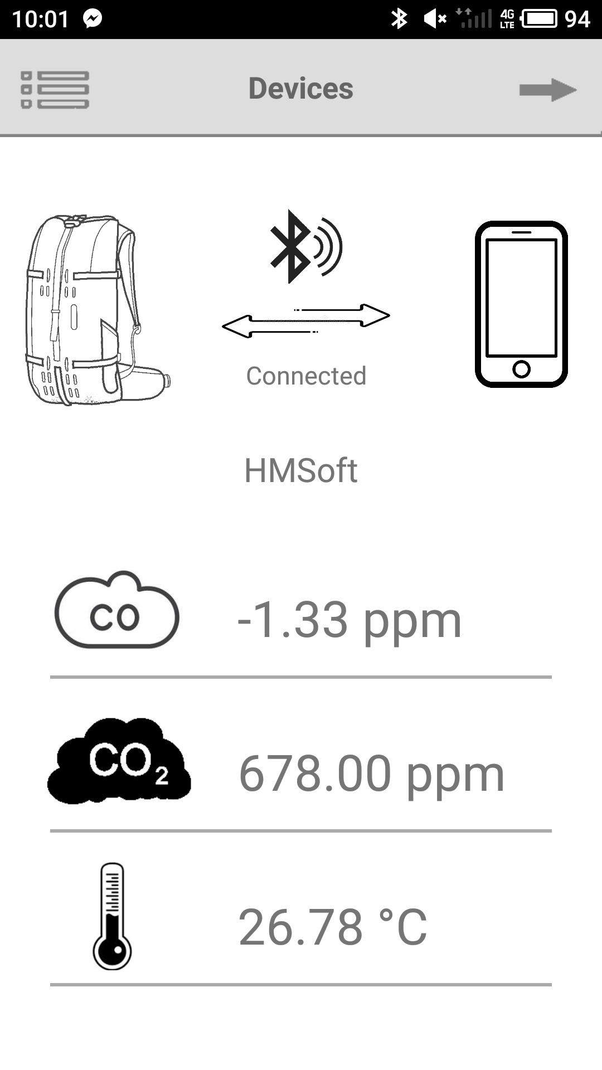
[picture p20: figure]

Lors de la première mise en route du système, l’application demande l’accès à la localisation. Cette autorisation est nécessaire à la communication Bluetooth entre le smartphone et le CarbOnFire.

Au démarrage de l’application aucun appareil n’est connecté. Il faut appuyer sur le bouton « DEVICE ». Une liste déroulante s’affiche alors, au fur et à mesure que de nouveaux appareils disponibles sont découverts.

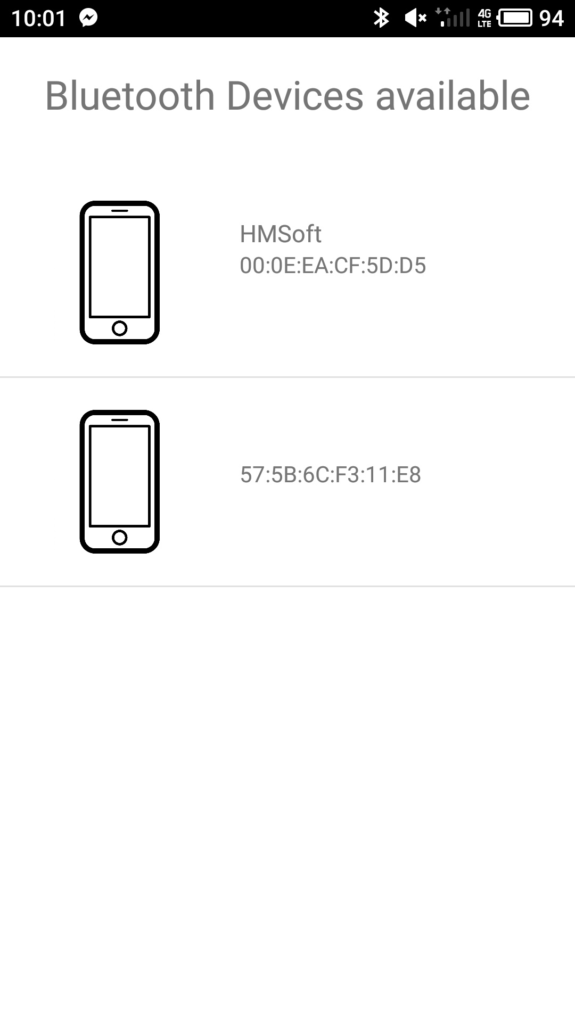
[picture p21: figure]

Lorsque l’utilisateur sélectionne un appareil, l’application tente de s’y connecter. L’utilisateur est notifié de cette tentative par un logo animé de chargement. À la fin du chargement, le nouvel état de connexion est affiché sur l’écran.

Si la connexion est établie, les mesures s’affichent et sont rafraîchies dès qu’une nouvelle trame est reçue.

Si le système de mesure se déconnecte, l’application notifie se changement d’état dans un délai de 8 secondes.

Vision globale de l’organisation du code JAVA

Si vous n’êtes pas familier avec le codage d’application Android, les concepts et objets utilisés sont expliqués dans les grandes lignes. Si vous souhaitez en savoir plus, des liens vers le site Android Devellopeur sont renseignés en note de bas de page.

L’application est composée de deux activités et de deux threads. Les threads et les activités sont deux types de classes Java. En d’autres termes, ce sont deux types de code Java qui ont des rôles bien définis et différents. Dans le cadre du projet, les activités sont les piliers de l’application. Elles ont pour rôle principal de gérer les interactions entre l’utilisateur, l’interface graphique et la logique de l’application. Ce sont en quelques sorte les chefs d’orchestre de l’application. Les threads quant à eux, contiennent du code qui s’exécute en parallèle des activités. Ils n’interagissent pas avec l’interface graphique et permettent de faire tourner un code annexe en parallèle de l’exécution de l’activité courante. Ils sont souvent utilisés pour exécuter des fonctions bloquantes en arrière-plan sans que l’interface graphique ne soit figée.

Le fait d’appartenir à une classe, permet de définir une fois pour toute des fonctions partagées par plusieurs codes de même nature. Prenons l’exemple de la classe activité. Dans la classe Activité, des fonctions sont déjà implémentées pour faciliter le codage de l’activité. On retrouve entre autres, des fonctions dites callback qui exécute un code, écrit par le développeur, à la suite d’un événement particulier. Par exemple la fonction onCreate() exécute un code, au lancement de l’activité.

Dans notre application, la première activité, MainActivity, gère l’interface principale qui est l’interface d’accueil où sont affichés l’état de connexion et ainsi que les dernières mesures reçues. La deuxième activité, ActivityDevice, gère l’interface de choix d’un appareil Bluetooth.

Pour ce qui est des threads, l’un d’eux, appelé ConnectThread, sert à effectuer une tentative de connexion avec un appareil Bluetooth. L’autre, MyBluetoothService, sert à assurer la communication Bluetooth avec un appareil connecté. Il reçoit les trames de mesures et les envoie à l’activité principale.

Scénario général de l’application

Au démarrage de l’application, la code de la MainActivity s’éxécute et l’utilisateur voit s’afficher l’écran d’accueil. Lorsque l’utilisateur appuie sur le bouton « DEVICE », il lance une nouvelle activité, l’activité ActivityDevice. Le lancement de la nouvelle activité s’accompagne d’un changement d’interface graphique. L’écran de choix d’appareil bluetooth est affiché. L’activityDevice débute dès son lancement par scanner les appareils Bluetooth visibles, et les affiche sur la liste au fur et à mesure de leur découverte. L’utilisateur peut sélectionner un appareil de la liste. Lorsqu’il le fait, l’ActivityDevice mémorise l’appareil sélectionné et le transmet à l’activité principale. L’activityDevice est alors arrêtée et l’utilisateur revient dans l’activité principale sur l’écran d’accueil.

Si l’utilisateur à choisi un appareil, l’activityMain démarre une tentative de connexion avec cet appareil. Elle utilise pour cela un thread ConnectThread. Le thread communique avec la MainActivity par le biais d’un objet Handler qui a le rôle de messager. Il permet l’échange d’informations entre les deux entités. En attendant des nouvelles du ConnectThread, l’ActivityMain continue de tourner normalement. Si un message informant le succès de la connexion avec l’appareil souhaité est reçu par l’activité, le ConnectThread est arrêté, et un nouveau thread, MyBluetoothDevice est lancé. Ce thread reçoit les séries de caractères envoyées par l’appareil Bluetooth couramment connecté. Il les transmet à la MainActivity dans des messages envoyés via le Handler. Ces séries de caractères sont recomposées par la MainActivity puis décodées pour en extraire les valeurs des mesures et les afficher.

Si la communication Bluetooth est interrompue, le trhead MyBluetoothService informe la MainActivity qui arrête le thread MyBluetoothService et notifie l’utilisateur.

Indication d’utilisation

Assemblage

Comme nous l’avons évoqué au début, le système est composé de quatre éléments installés sur le sac à dos : la batterie, la pompe, le compteur à gaz et le boîtier de mesure. Le sac à dos comporte deux étages. Sur le premier étage est placée la pompe, vissée sur la plaque, et la batterie, maintenue par un élastique. Sur le deuxième étage est fixé le compteur à gaz. La fixation du boîtier de mesure n’est pas encore défini. Pour les tests il est scotché sous la plaque du deuxième étage.

Une fois que tous les éléments sont fixés, on peut brancher le circuit d’air. Le long tuyau équipé du porte-filtre à une extrémité, est branché par l’autre extrémité sur l’entrée de la pompe.

La sortie de la pompe est branchée par un petit tuyau au connecteur gauche du boîtier de mesure.

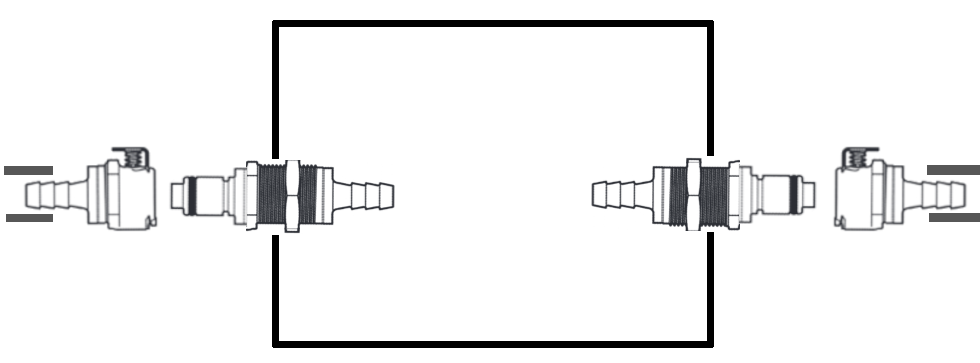
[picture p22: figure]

Enfin le connecteur droit du boîtier est branché à l’entrée du compteur à gaz.

Mise en route du système

Avant de mettre en route le système, il faut vérifier qu’il est bien branché. Un câble doit partir de la batterie et arriver sur le prise d’entrée d’alimentation du boîtier. C’est un câble cosse vers prise CC.

Photo branchement alimentation boitier

Ensuite il faut brancher la pompe à la prise de sortie du boitier. Pour cela on utilise le câble cosse mal vers prise CC.

Photo branchement alimentation pompe

A ce stade, si vous actionnez le bouton ON/OFF du système de mesure, la led verte devrais s’allumer. Cela signifie que le système de mesure est actif. Si vous appuyez sur le bouton ON/OFF de de la prise d’alimentation de la pompe, la pompe devrais s’allumer. Si ce n’est pas le cas, laisser le bouton sur ON et actionnez l’interrupteur situé directement sur le câble de la pompe. A noter que la led verte prévu pour la pompe n’est pas branchée car ses pattes de connexion sont cassées, elle sera donc toujours éteinte.

Connexion avec l’application

Pour visualiser les mesures vous pouvez télécharger l’application CarbOnFire. Pour cela, rendez-vous sur le github à l’URL : le ReadMe de l’application contient toutes les instructions d’installations.

Lorsque vous lancer l’application pour la première fois, il vous ait demandés la permission d’accès à la localisation. Cette autorisation est nécessaire pour le fonctionnement du bluetooth. Il vous faut l’accepter sinon l’application ne marchera pas. Pour se connecter au boîtier, appuyer sur le bouton « DEVICE ». Une liste déroulante s’affiche avec les appareils Bluetooth détectés. Sélectionnez celui correspondant au boîtier. Par défaut, son nom est HMSOFT. Attendez que la connexion se fasse.

Dès que le système de mesure est connecté, les mesures s’affichent et se mettent à jour automatiquement.

Récupération des données

Pour récupérer les données après une mesure, il faut retirer la carte SD. Pour cela il faut commencer par extraire le boitier du sac à dos, puis dévisser les quatre vis de fixation du couvercle. Enlevez le couvercle et la carte SD est directement accessible sur le shieldSD.

Réglage de la RTC

Il est possible que la RTC se dérègle (plus de pile, dérive de l’heure avec le temps), il faut alors la remettre à l’heure. Pour ce réglage il faut branché à un PC le shield SD monté sur une carte arduino uno. Il y a plusieurs options, soit vous branchez directement le carte arduino uno du boitier sans rien démonter, soit vous extrayez uniquement le shield SD du boitier et le monté sur une autre carte arduino uno extérieur au boitier. Il vous faut ensuite lancer le programme de calibration de la rtc disponible sur le github. Lisez le ReadMe associé pour plus de détail.

Si vous utiliser la carte arduino du boîtier pour régler l’adc, n’oubliez pas de retéléverser le programme principale sur la carte, une fois le réglage terminé.

Problème pouvant être rencontrés

Le boitier n’est pas visible en Bluetooth : Ouvrez le boîtier et vérifier l’état de la led jaune du module bluetooth.

Photo led jaune module bluetooth

Si elle clignote, le problème vient du smartphone. Essayer de redémarrer l’application puis si ça ne fonctionne pas, redémarrez votre téléphone.

Si elle reste allumée, cela veut dire qu’un autre appareil Bluetooth est connecté au module. Vous pouvez essayer d’éteindre le boitier et le rallumer pour réinitialiser le bluetooth.

Si elle est éteinte, cela veut dire qu’il y un problème dans le branchement. Vérifiez que les câbles soient bien branchés.

Le boîtier est connecté en Bluetooth mais les mesures ne s’affichent pas : Cela veut dire qu’il y a un problème dans l’initialisation du programme.

- vérifiez que la carte SD est bien présente.

- vérifiez que l’adc et le BMP280 sont bien branchés (pour le détail des branchement voir partie circuit electrique dans construction du boitier de mesure).

Construction du boîtier de mesure

Avant de construire le système veillez à lire tout lire, et en particulier la dernière partie sur les conseil de construction.

Perçage du boîtier

Le boitier est percé en face avant pour accueillir les éléments du panneau avant : boutons, LED, prises et porte-fusible. Voici le schéma avec les cotations :

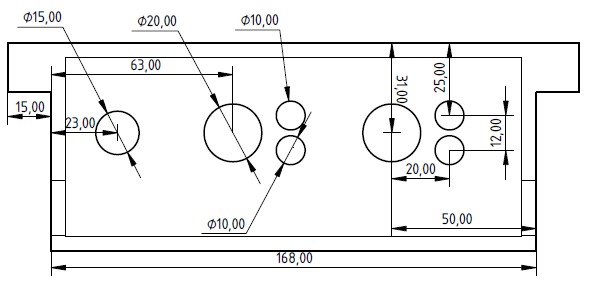
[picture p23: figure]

Le boitier est aussi percé sur les cotés pour accueillir les connexions rapides pour les tuyaux. Voici les cotations :

Le boîtier est percé au fond pour fixé les supports :

Enfin, il faut glisser le joint fourni avec le boitier dans la rainure du couvercle.

Cloison horizontale

La cloison horizontale est fabriquée à partir d’une grande plaque de PVC épaisse de 3mm. Voici les cotation de perçage :

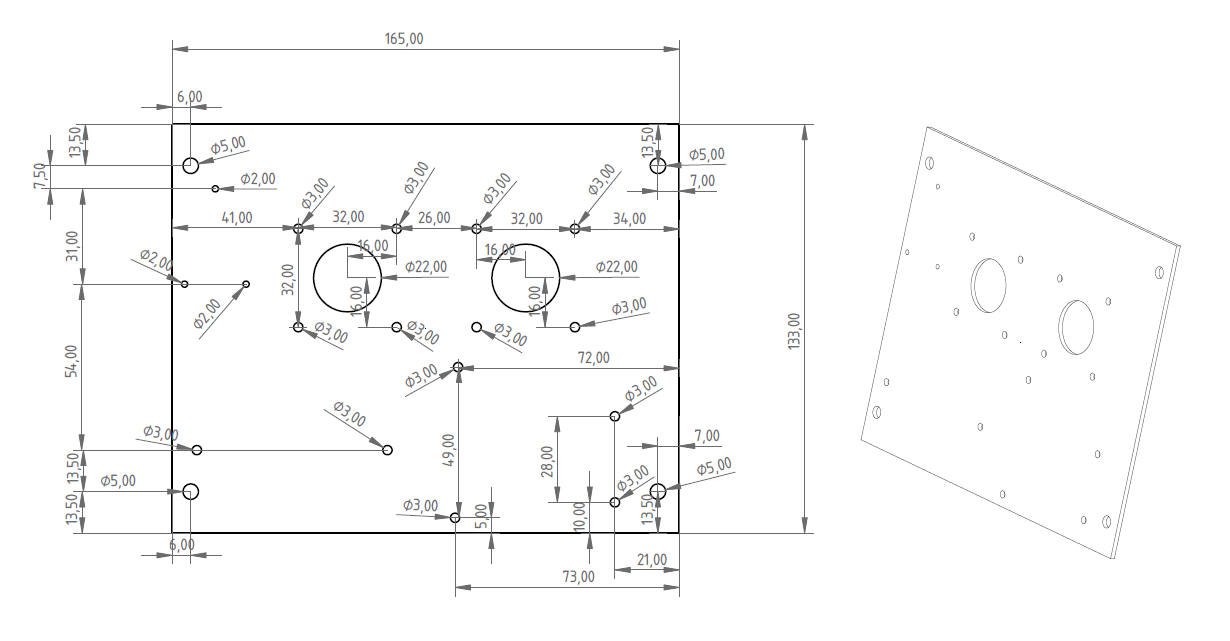
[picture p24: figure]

Support cloison

La cloison est supportée par deux piliers longitudinale. Les piliers sont fixés par des vis M3 avec le fond du boîtier et par des vis M5 avec la cloison. Voici les cotations :

Les trous des vis sont filetés. Pour réaliser ces trous, il faut percer le pilier avec les cotations présentes sur le schéma. Puis il faut tarauder le trou avec des tarauds M3 ou M5 en fonction du trou.

Panneau avant

Les éléments du panneau avant sont insérer dans leurs trous respectifs puis fixés par deux méthodes différentes. Les boutons sont uniquement clipsés, tandis ce que les autres éléments sont serrés sur la paroi par un système de vis-écrous. Voici la disposition des éléments

Circuit électrique

Shield SD

Le shield SD contient une zone libre pour faire des soudures. Pour le système 2 port groves y sont soudés. Le premier permet la connexion i2C avec les capteurs tandis ce que l’autre permet la connexion UART avec le module bluetooth. Le pas de la plaquette de soudure du shield est de 2,54mm alors que le pas du connecteur grove n’est que de 1,2mm. Pour cette raison il est nécessaire de plier légèrement les pattes du connecteur pour les insérer dans la plaquette de soudure.

Les deux connecteur sont placé l’un en face de l’autre comme montré sur la photo. Les connexions avec les pins de la carte arduino sont effectué sur la face arrière Voici le scéhma du montage :

Image soudure shield SD

PCB adc

Les circuits électriques extérieurs aux différentes cartes sont installés sur un PCB conçu spécialement pour le projet. Il est composé d’un bornier de 14 fils, de deux port grove i2c, d’une fiche de connexion pour l’adc adafruit, de deux connecteur molex pour le capteur de CO et celui de CO2, et une prise CC d’alimentation 12V pour la carte arduino.

photo PCB

Le bornier sert à connecter les 7 dipôles du panneau de mesure. Les deux connecteurs grove i2c sont connectés ensemble. L’un deux sert à connecter le BMP280, l’autre sert à connecter l’ensemble du bus i2c à la carte arduino. Le connecteur molex 4-pin est utlisé pour connecter le capteur de CO2. Le circuit de mesure présenté dans la partie mesure de CO2 est imprimé sur le PCB. Le connecteur molex 2-pin est utilisé pour connecter le capteur chimique de CO. Le circuit de mesure présenté dans la partie mesure de CO est également imprimé sur le PCB.

L’adc adafruit vient se brancher dans la fiche de connexion prévue pour. Le PCB contient le circuit électrique permettant d’une part de connecter l’adc au bus i2c et d’autre part de connecter les voies 0 et 1 aux tensions de mesure des capteurs de CO et CO2.

Voici le schéma électrique, le masque du PCB ainsi que le schéma de soudure :

circuit électrique, schéma de soudure, masque PCB

Câbles de connexion

Pour assurer les connexions entre les éléments, 3 types de câbles sont utilisés. Les câbles présents entre le panneau avant et le bornier de connexion du PCB sont des câbles à plusieurs brins, coupés sur mesure. Les câbles grove sont des câbles de taille standard pré-assemblé. Les câbles molex sont des câbles à sertir. Ils doivent être assemblé avant de pouvoir être utilisé. Ils sont composé de 3 pièce détachées : les fils, les boîtiers de connecteurs et les contacts à sertir. Il faut dans un premier temps sertir les contact sur les fils, puis engager les contacter dans les boîtiers de connecteurs :

Schéma contact à sertir

Câblage des éléments électriques

Une fois que tous les éléments sont prêts, il faut les brancher. Le mieux est de commencer par le panneau avant. Les câble du panneau avant sont soudés sur les broches de connexion de chacun des éléments du panneau. Les autres extrémités des fils sont insérer dans leur emplacements respectifs dans le bornier puis visser. La taille de chaque câble est ajusté sur mesure pour limiter le volume de câble dans le boîtier. Voici le schéma de connexion du bornier :

schéma de connexion du bornier

Les deux bornes des boutons et du porte-fusible sont équivalentes, il n’y a pas d’ordre de connexion. En revanche pour les led et les prise d’alimentation, il faut repérer la nature des bornes. Pour les led, une inversion des bornes n’impactera pas le système, mais la led ne s’allumera pas. Pour les prises d’alimentation, un inversion des bornes peut endommager le système. Voici le descriptif des broches des prises d’alimentation :

schéma borne prise CC

Une fois que le bornier est connecté au panneau de face avant, il faut connecter les capteurs. Les deux câbles molex, doivent être connecté chacun sur leur capteur respectif. Un cable grove i2x est branché entre le capteur de BMP280 et un des port i2c du PCB. L’autre cable grove i2c est connecté entre le deuxième port i2c du PCB et le port i2c soudés sur le shield SD. Le connecteut CC du PCB est connecté au port jack de l’arduino. L’adc est encastré dans les fiches de connexion qui lui sont dédiées. Enfin le connecteur grove UART du module Bluetooth est branché sur le port UART soudé sur le shield SD.

Photo branchement final

Assemblage du boîtier

Les composants électrique sont fixés sur la cloison par un système de vis écrou. Ils sont tous fixés sur la face supérieur de la cloison à exception du BMP280 qui est fixé sous la cloison. Le BMP280 et le module Bluetooth sont fixés de part et d’autre de la cloison par les trois mêmes vis.

La cloison est fixée sur ses piliers par 4 vis M5 en polyester.

Schéma de fixation cloison – piliers

Les piliers sont fixés au boîtier par 4 vis M3 :

schéma fixation boîtier - piliers

Conseil d’ordre de construction

Pour la construction du boîtier, il est nécessaire de commencer par la fabrication séparées des éléments mécaniques et électriques, à savoir le perçage du boîtier, la fabrication de la cloison et ses support, l’impression du PCB et le soudage des connecteurs grove sur le shield SD. Ensuite, il est conseillé de suivra l’ordre d’assemblage suivant :

1 - fixez les piliers avec le boîtier, en mettant sous le pilier, et surtout au niveau des deux trous, une couche de silicone pour assurer l’étanchéité de la fixation.

2 - fixez des embouts PLC traverse cloison sur le boitier. Avant de serrer l’écrou, appliquer une couche de silicone en bordure du trou pour assurer l’étanchéité.

3 - installez les éléments du panneau avant et mettre une couche de silicone pour assurer l’étanchéité.

4 - soudez les fils de connexion sur les broche du panneau avant en prévoyant large pour la taille du fil.

5 - fixez les éléments électriques sur la cloison horizontale.

6 - branchez le module bluetooth au shield SD.

7 - fixez la cloison sur les piliers

8 - branchez les fils du panneau avant en les faisant passer derrière le module bluetooth. Ajustez la taille de chaque fil pour qu’il soit juste assez long pour atteindre son emplacement dans le bornier.

9 - branchez les autres cables.

10 - placez le joint dans la reinure du couvercle. Apliquer un point de sylicone à la jonction des deux bouts de joints.

11 – Fermez le boîtier avec les 4 vis cruciforme.

Remarques et Perspectives

Annexe

datasheet capteur et carte d’acquisition

liste des pièces et référence

bibliographie

thèse

github

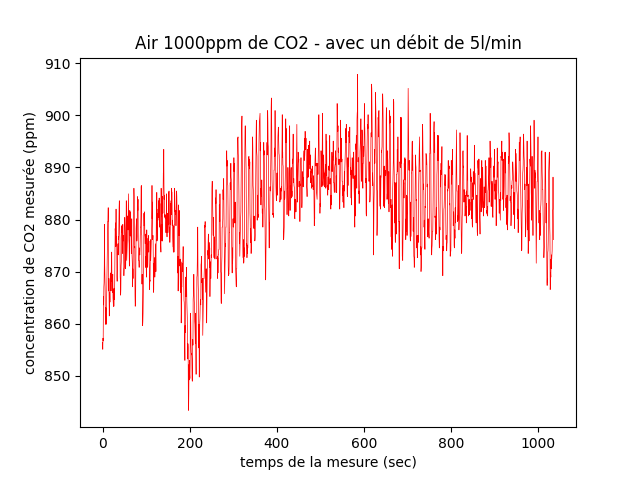
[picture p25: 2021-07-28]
Mesures/Etalonnage_22-07-21/courbes/figure_de_CO2_1000ppm_5lmin.png

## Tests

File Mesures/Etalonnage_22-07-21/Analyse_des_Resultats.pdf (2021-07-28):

# R´esultats d’´etalonnage du 22/07/21

Capteurs de CO et CO2

## 1 Montage de l’exp´erience

Pour r´ealiser l’´etalonnage des capteurs, nous avons utilis´e la premi`ere version du boˆıtier de mesure CarbOn-Fire. Nous avons inject´e diff´erents types d’air avec des concentrations contrˆol´ees pour les gaz mesur´es. Pour les mesures d’air z´ero, nous utilisons l’air de la pi`ece `a laquelle nous retirons le CO ou le CO2 avec des bonbonnes qui fixent respectivement le CO et le CO2

Pour les concentrations plus ´elev´ees, nous utilisons des bouteilles directement branch´ees sur le boˆıtier de mesure avec un d´ebit r´egl´e en amont. Voici le r´esum´e des r´esultats obtenus.

## 2 Capteur de CO

### 2.1 Etalonnage `a 0ppm de CO ´

Pour la premi`ere exp´erience, nous avons inject´e de l’air avec une concentration en CO inf´erieure `a 1bpm, bien inf´erieure `a la pr´ecision du capteur (3ppm). La concentration initiale avant injection ´etait de 15ppm. Voici les r´esultats obtenus :

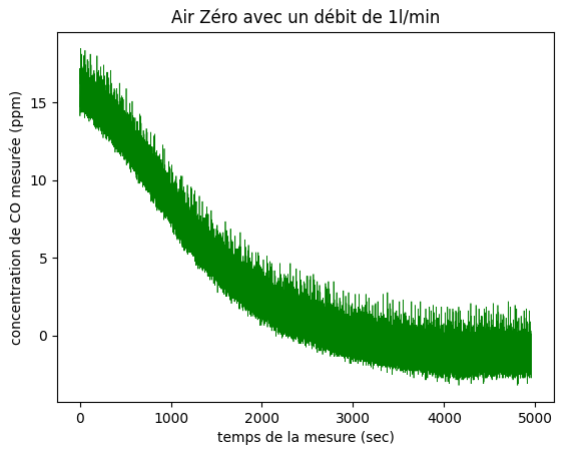
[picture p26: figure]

Figure 1: ´etalonnage du 0ppm de CO `a 1l/min

La mesure du z´ero, se stabilise l´eg`erement en dessous de 0ppm `a environ -2ppm. Cela peut venir de diff´erents param`etres, la d´erive en temp´erature, la mauvaise pr´ecision de l’ADC ou le mauvais ´etalonnage du capteur. Dans tous les cas cette erreur repr´esente 0,2% d’erreur par rapport `a la valeur maximale du capteur. Nous pouvons donc consid´erer que cette erreur est acceptable.
Le temps de r´eponse du syst`eme est d’environ 4000 secondes ce qui est trop pour l’application souhait´ee. Ce d´elai peut ˆetre li´e `a diff´erents param`etres, comme le volume important du boˆıtier, le d´ebit trop faible du flux d’air ou la position du capteur. Une solution envisageable serait d’ajouter un conduit avec les capteurs `a l’int´erieur.
Concernant la position du capteur, le temps de r´eponse serait plus court si le capteur ´etait plac´e directement dans le flux d’air. Il faut v´erifier que la pr´ecision de la mesure n’est pas impact´ee par la vitesse du flux laminaire.

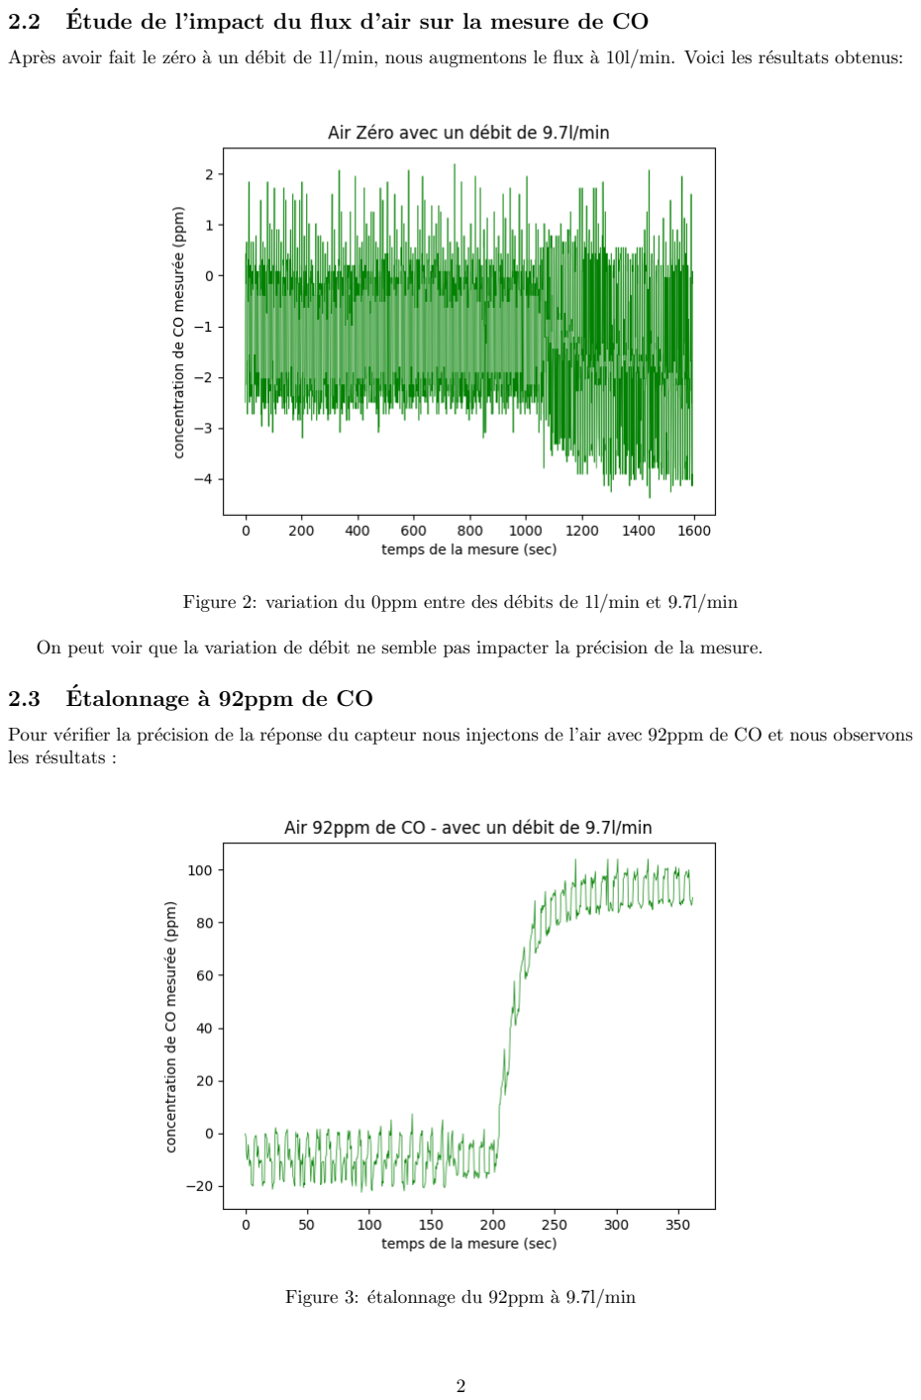
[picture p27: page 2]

### 2.2 Etude de l’impact du flux d’air sur la mesure de CO ´

Apr`es avoir fait le z´ero `a un d´ebit de 1l/min, nous augmentons le flux `a 10l/min. Voici les r´esultats obtenus:

Figure 2: variation du 0ppm entre des d´ebits de 1l/min et 9.7l/min

On peut voir que la variation de d´ebit ne semble pas impacter la pr´ecision de la mesure.

### 2.3 Etalonnage `a 92ppm de CO ´

Pour v´erifier la pr´ecision de la r´eponse du capteur nous injectons de l’air avec 92ppm de CO et nous observons les r´esultats :

Figure 3: ´etalonnage du 92ppm `a 9.7l/min

La pr´ecision de la mesure est du mˆeme ordre que pour l’´etalonnage du 0ppm, soit d’environ 3ppm. Le temps de r´eponse en revanche est plus rapide, environ 50 secondes.

## 3 Capteur de CO2

### 3.1 Etalonnage `a 0ppm de CO2 ´

Comme pour le CO, nous injectons de l’air dont la concentration en CO2 est de l’ordre du bpm. Pour cette exp´erience, nous n’avions pas d’instrument pour contrˆoler la concentration en CO2. Le z´ero, a ´et´e effectu´e avec une bonbonne qui fixe le CO2. Nous ferons l’hypoth`ese que la concentration en CO2 est inf´erieure `a la pr´ecision du capteur (30ppm). Voici les r´esultats :

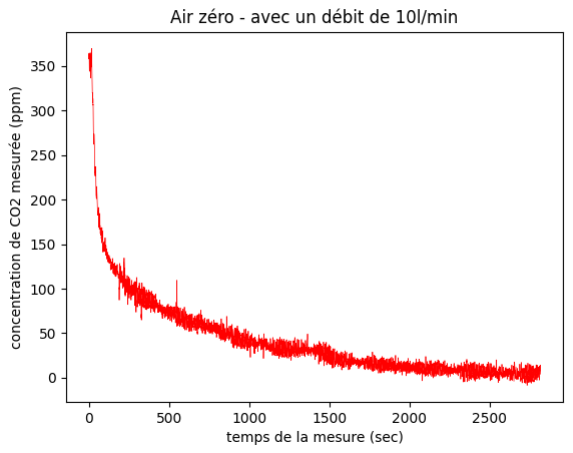
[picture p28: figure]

Figure 4: ´etalonnage du 0ppm `a 10l/min

On voit que la pr´ecision du z´ero est satisfaisante puisqu’elle est d’environ 5ppm plus ou moins 10ppm. Nous sommes inf´erieurs `a la pr´ecision du capteur qui est de 30ppm.

Le temps de r´eponse est 2 fois moins long que pour celui du CO, mais il est toujours trop long : 25000 secondes. Mˆeme remarque que pour le CO.

### 3.2 Etude de l’impact du d´ebit sur la mesure ´

Comme pour le CO, dans le but d’am´eliorer le temps de r´eponse du syst`eme, il serait int´eressant de placer le capteur directement dans le flux d’air. Il faut alors v´erifier l’impact du flux sur la mesure de CO2. Pour cela nous avons mesur´e la variation de la mesure entre un z´ero `a 10l/min et un z´ero `a 5l/min :

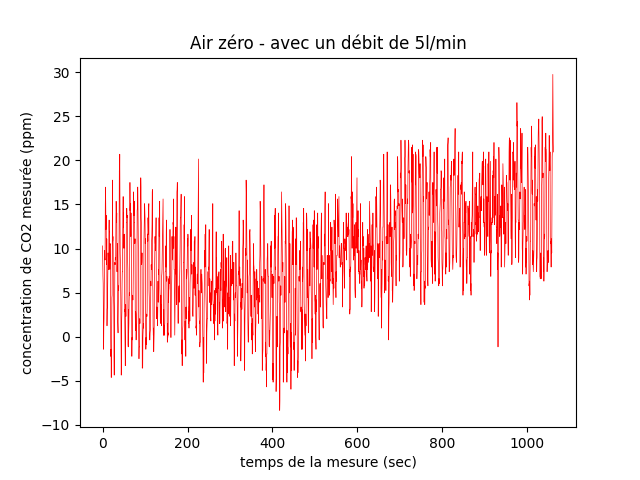
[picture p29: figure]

Figure 5: variation du 0ppm entre des d´ebits de 5l/min et 10l/min

On voit qu’il y a une l´eg`ere variation d’environ 5 ppm sur la mesure de CO2 pour une variation de d´ebit de 10l/min `a 5l/min. Cette variation semble ˆetre inf´erieure `a la pr´ecision du capteur mais on pourrais faire une analyse plus pouss´ee pour ´etablir un algorithme de correction de la mesure en fonction du d´ebit.

### 3.3 Etalonnage `a 1000ppm de CO2 ´

Nous ´etudions dans cette derni`ere exp´erience la r´eponse du syst`eme `a un ´echelon de 1000ppm de CO2. Voici les r´esultats :


Figure 6: ´etalonnage du 1000ppm `a 10l/min

On voit qu’il y a un d´ecalage de 100ppm entre la r´eponse du capteur et la valeur r´eelle de CO2. Cela peut venir du mauvais ´etalonnage du capteur ou de la d´erive en temp´erature. Il faudrait ´etudier plus en d´etail ce ph´enom`ene pour ´etablir un algorithme de correction.
Le temps de r´eponse est en revanche convenable, la valeur stable `a 5% est atteinte en 50 secondes.

## 4 Conclusion

Pour les deux capteurs, il y a une forte instabilit´e de la mesure `a 1% de la valeur maximale des capteurs. Ce fort bruit pourrais venir de l’ADC dont la pr´ecision est de l’ordre de la centaine de micro Volts.
La pr´ecision du capteur de CO semble convenable (de l’ordre de 5ppm). Malgr´e tout, il y a des axes d’am´elioration : notamment l’int´egration d’une correction en temp´erature.
La pr´ecision du capteur de CO2 est insuffisante. On observe un ´ecart de 100ppm pour une concentration r´eelle de 1000ppm. Il faut ´etablir un algorithme de correction et ´etudier la d´erive de la r´eponse en fonction de la concentration r´eelle et de la temp´erature.
Enfin, le temps de r´eponse du syst`eme est convenable pour des concentrations ´elev´ees mais trop longue pour des concentrations autour de 0ppm. Sachant que le syst`eme sera utilis´e pour mesurer des concentrations ´elev´ees, le temps de r´eponse est convenable. Malgr´e tout, il est possible d’am´eliorer ce temps de r´eponse en modifiant la disposition des capteurs et en diminuant le volume de la chambre de mesure.

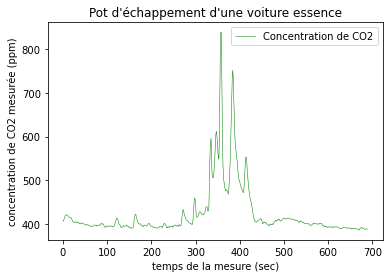
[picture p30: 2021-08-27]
Mesures/Tests_en_conditions_réels_27-08-21/Courbes/Pot d'échappement d'une voiture essence_CO2_Q-Track.png

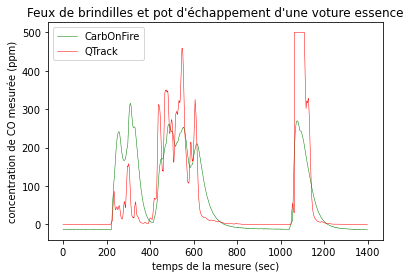
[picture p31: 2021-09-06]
Mesures/Tests_en_conditions_réels_27-08-21/Courbes/figure_CO.png

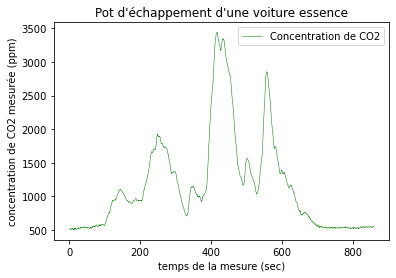
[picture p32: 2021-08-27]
Mesures/Tests_en_conditions_réels_27-08-21/Courbes/Pot d'échappement d'une voiture essence_CO2_CarbOnFire.png

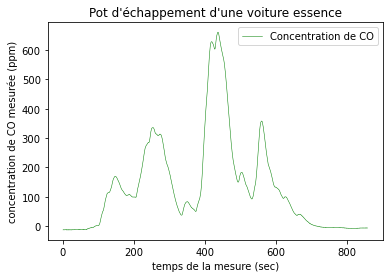
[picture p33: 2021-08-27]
Mesures/Tests_en_conditions_réels_27-08-21/Courbes/Pot d'échappement d'une voiture essence_CO_CarbOnFire.png

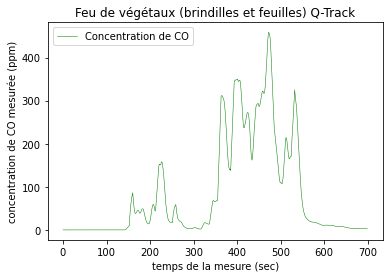
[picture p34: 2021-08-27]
Mesures/Tests_en_conditions_réels_27-08-21/Courbes/Figure 2021-08-27 173205 (0).png

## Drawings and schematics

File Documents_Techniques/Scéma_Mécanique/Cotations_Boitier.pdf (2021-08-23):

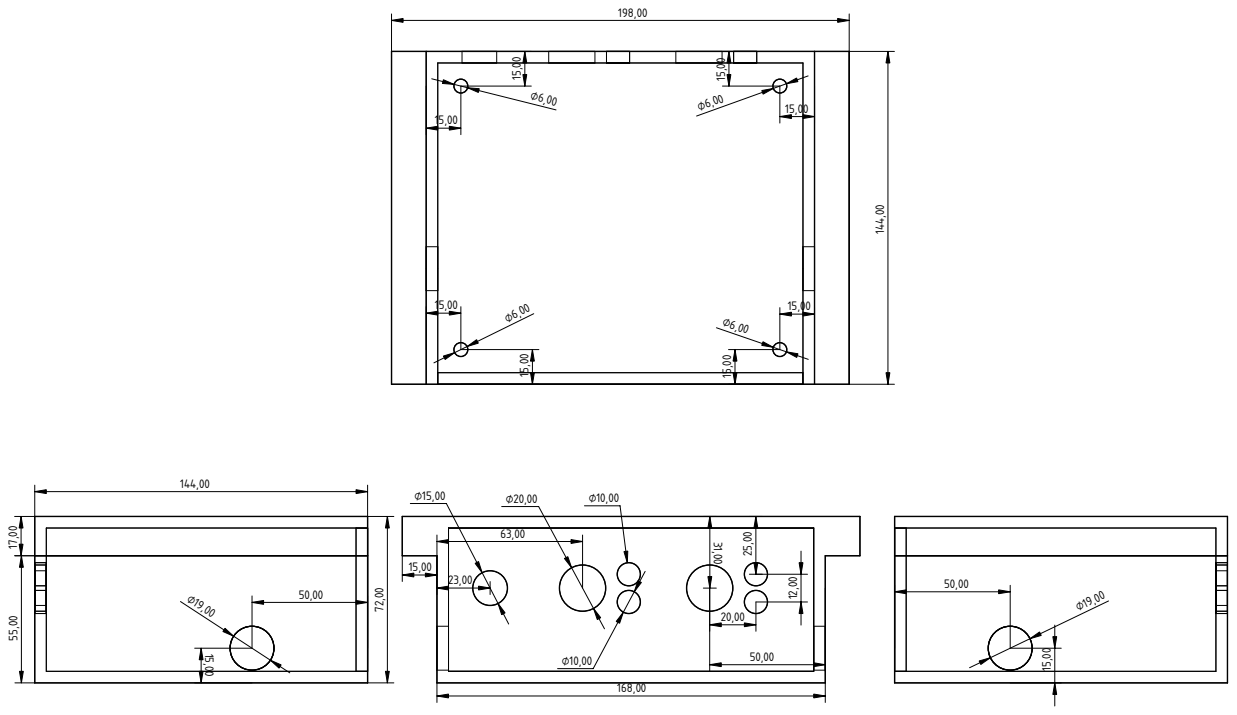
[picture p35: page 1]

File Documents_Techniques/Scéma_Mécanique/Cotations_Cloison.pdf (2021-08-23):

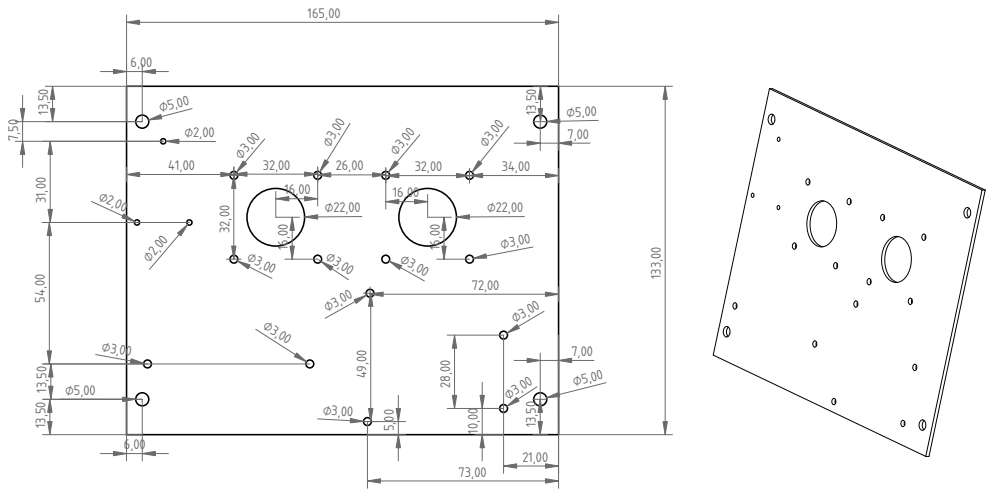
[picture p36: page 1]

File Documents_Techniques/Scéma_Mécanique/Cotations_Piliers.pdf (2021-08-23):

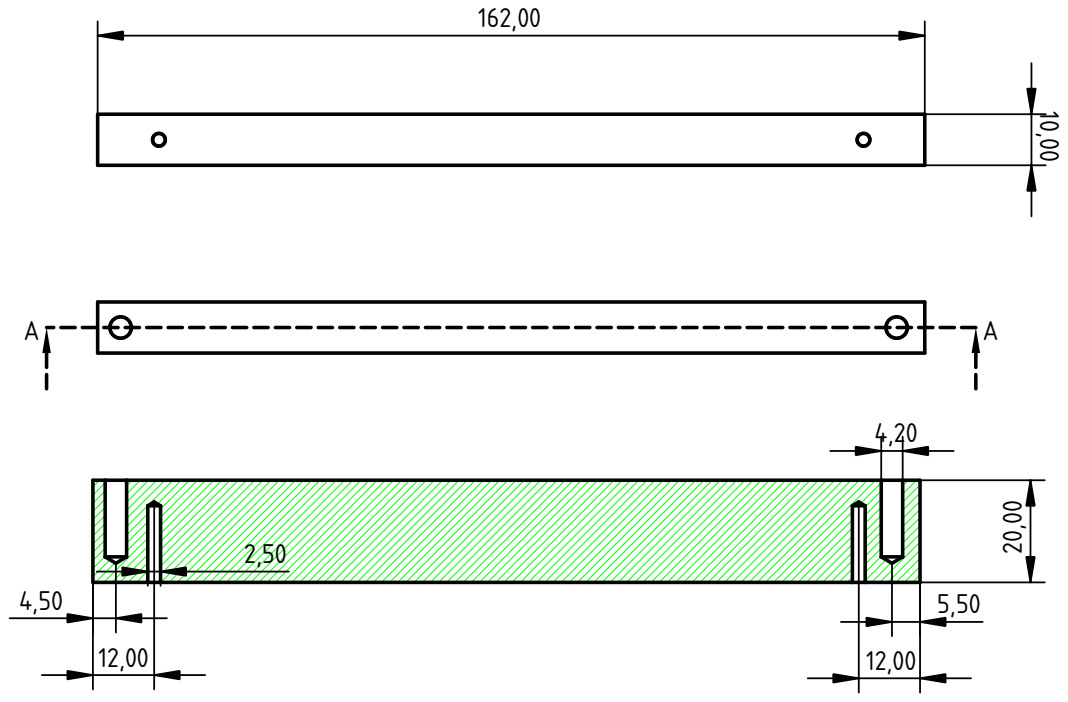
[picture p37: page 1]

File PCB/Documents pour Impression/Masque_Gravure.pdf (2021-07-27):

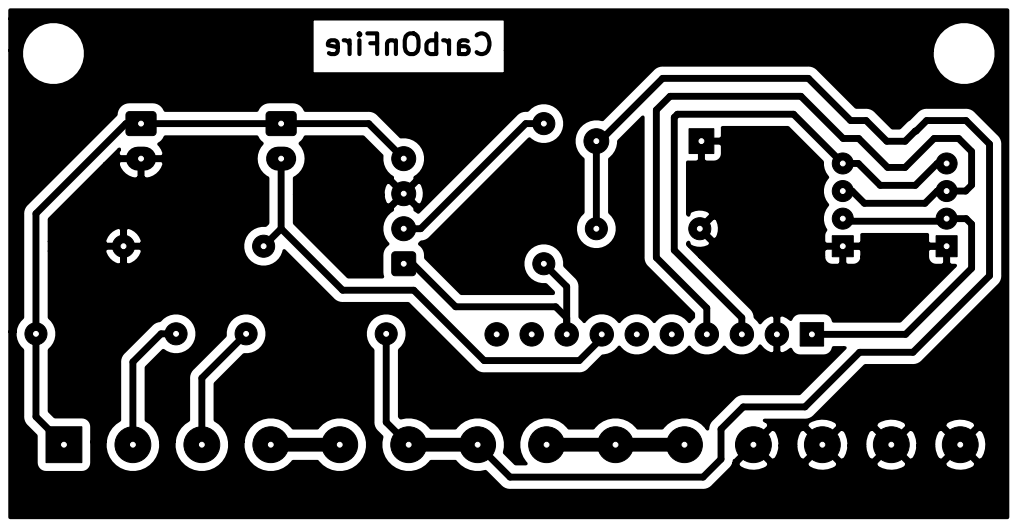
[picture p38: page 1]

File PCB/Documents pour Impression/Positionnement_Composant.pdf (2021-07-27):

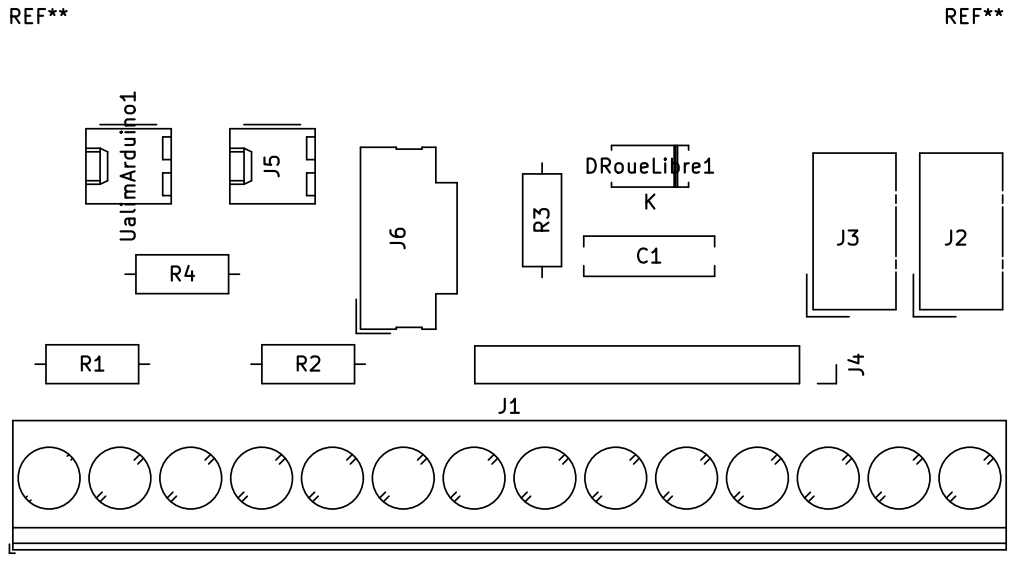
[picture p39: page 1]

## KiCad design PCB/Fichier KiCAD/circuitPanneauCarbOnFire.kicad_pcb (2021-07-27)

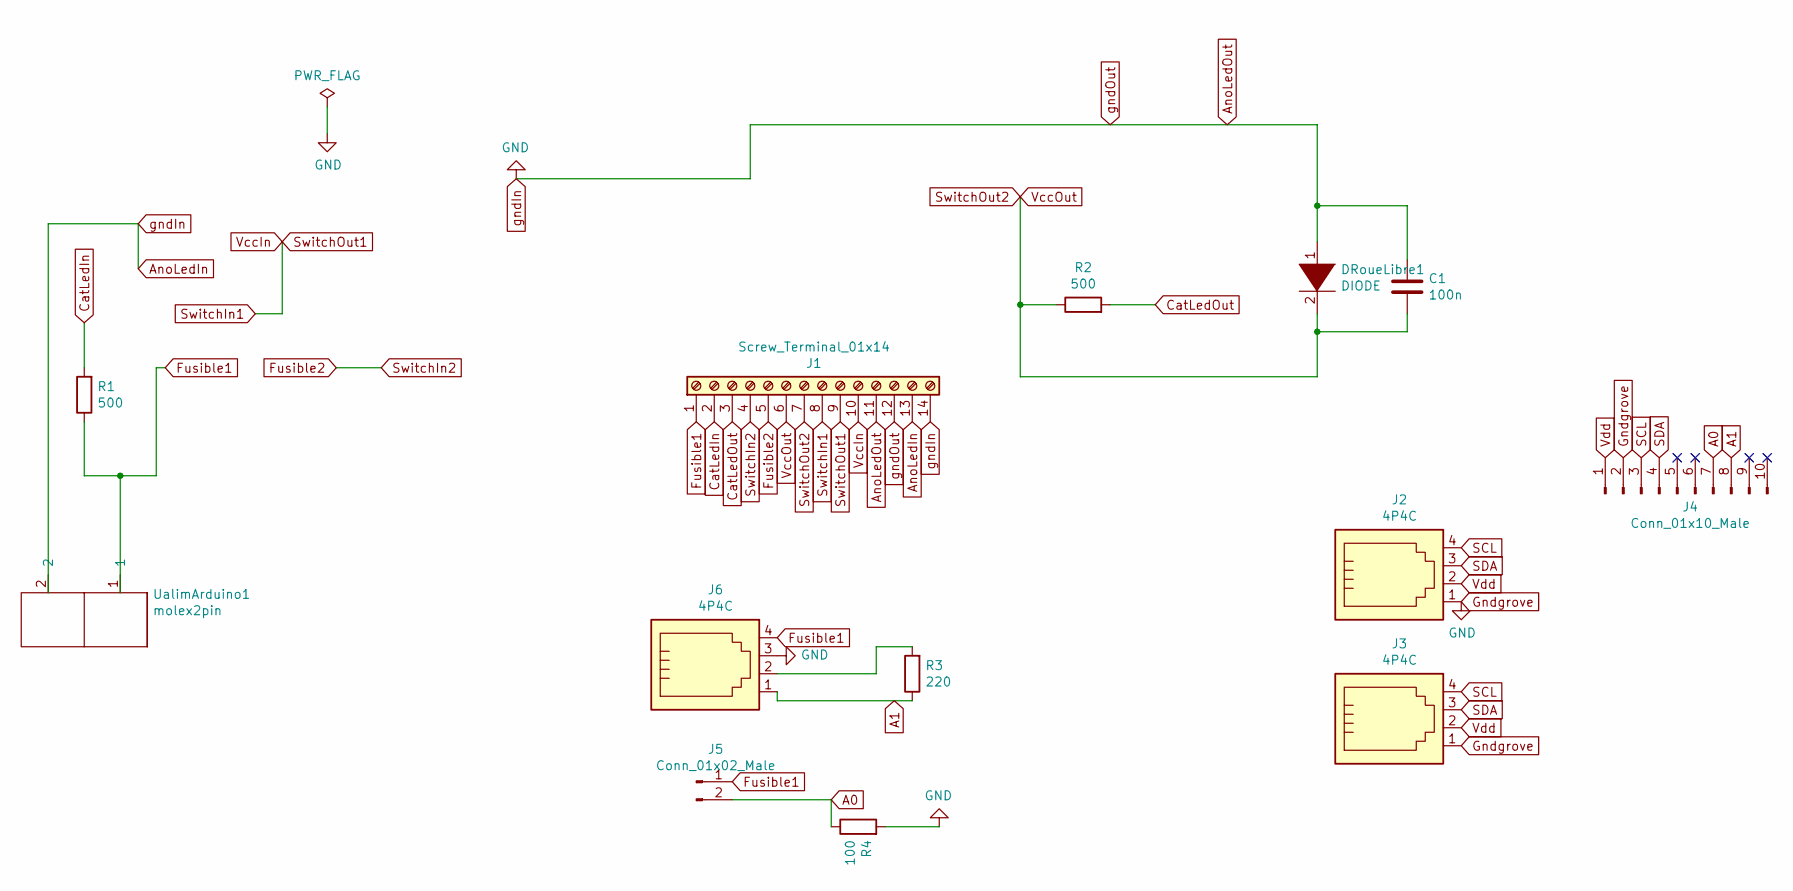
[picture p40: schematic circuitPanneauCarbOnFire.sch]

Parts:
C1: 100n; C_Rect_L9.0mm_W2.6mm_P7.50mm_MKT
DRoueLibre1: DIODE; D_A-405_P7.62mm_Horizontal
J1: Screw_Terminal_01x14; TerminalBlock_Phoenix_PT-1,5-14-5.0-H_1x14_P5.00mm_Horizont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
J2, J3: 4P4C; NS-Tech_Grove_1x04_P2mm_Vertical
J4: Conn_01x10_Male; PinSocket_1x10_P2.54mm_Vertical
J5: Conn_01x02_Male; Molex_KK-254_AE-6410-02A_1x02_P2.54mm_Vertical
J6: 4P4C; Molex_SL_171971-0004_1x04_P2.54mm_Vertical
R1, R2: 500; R_Axial_DIN0207_L6.3mm_D2.5mm_P10.16mm_Horizontal
R3: 220; R_Axial_DIN0207_L6.3mm_D2.5mm_P10.16mm_Horizontal
R4: 100; R_Axial_DIN0207_L6.3mm_D2.5mm_P10.16mm_Horizontal
UalimArduino1: molex2pin; Molex_KK-254_AE-6410-02A_1x02_P2.54mm_Vertical

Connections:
A0: J4.7, J5.2, R4.1
A1: J4.8, J6.1, R3.1
AnoLedIn: C1.2, DRoueLibre1.1 (K), J1.11, J1.12, J1.13, J1.14, J2.1, J3.1, J4.2, J6.3, R4.2, UalimArduino1.2
CatLedIn: J1.2, R1.2
CatLedOut: J1.3, R2.2
Fusible1: J1.1, J5.1, J6.4, R1.1, UalimArduino1.1
Fusible2: J1.4, J1.5
unnamed: J6.2, R3.2
SCL: J2.4, J3.4, J4.3
SDA: J2.3, J3.3, J4.4
SwitchIn1: J1.8, J1.9, J1.10
SwitchOut2: C1.1, DRoueLibre1.2 (A), J1.6, J1.7, R2.1
Vdd: J2.2, J3.2, J4.1

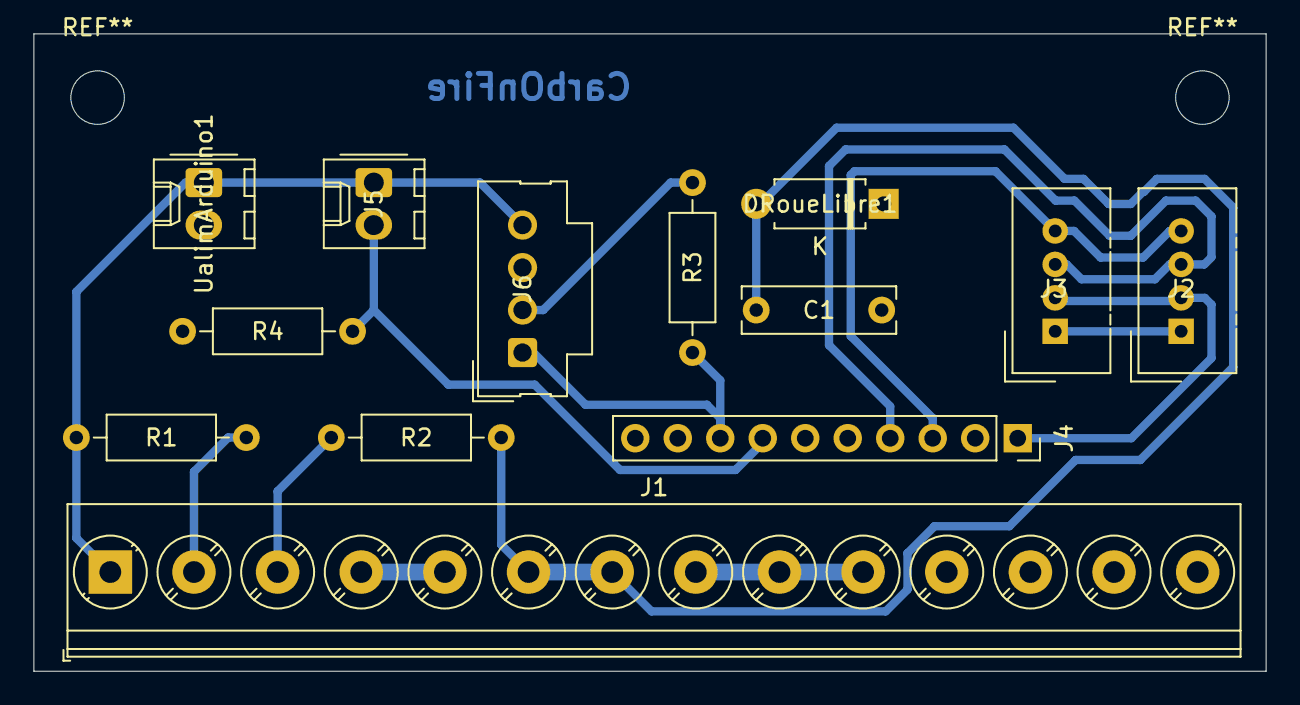
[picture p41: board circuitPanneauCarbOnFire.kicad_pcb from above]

Board: 2 copper layers, 73.7 x 38.1 mm, 13 parts (0 on the bottom side), 13 nets.

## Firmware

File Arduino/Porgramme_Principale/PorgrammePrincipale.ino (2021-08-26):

//Librairie

#include <SD.h>
#include <BMP280_DEV.h>
#include <MD_DS1307.h>
#include <Wire.h>
#include <Adafruit_ADS1X15.h>



// Constantes 

#define DATA_DIR "DONNEE"
#define TAILLE_TABLEAU 11
#define R_CO 99  //Resistance de Mesure du CO
#define R_CO2 220 //Resistance de Mesure du CO2
#define COPin 0   // Pin de lecture du CO
#define CO2Pin 1  // Pin de lecture du CO2
#define PERIODE_ECHANTILLONAGE 500 // en millisecondes



//Variables 

Adafruit_ADS1115 ads;
float temperature, pressure, altitude, CO2, CO;
double Tab_Mesure[TAILLE_TABLEAU];
File donnee;
BMP280_DEV bmp280;   // Instantiate (create) a BMP280_DEV object and set-up for I2C operation (address 0x77)



//Fonctions

float ConcentrationCO() {
  
  //transforme la mesure analogique en une valeur de ppm
  float mesure = ads.computeVolts(ads.readADC_SingleEnded(COPin));
  float mCO = 0;
  mCO = (mesure / R_CO - 0.004) * (5000 / 0.016);
  return mCO;
}

float ConcentrationCO2() {
  
  //transforme la mesure analogique en une valeur de ppm
  float mesure = ads.computeVolts(ads.readADC_SingleEnded(CO2Pin));;
  float mCO2 = 0;
  mCO2 = (mesure/ R_CO2 - 0.004) * (5000 / 0.016);
  return mCO2;
}


void InitialiserTabMesure(double Tab[TAILLE_TABLEAU]) {
  for (int i = 0; i < TAILLE_TABLEAU; i++) {
    Tab[i] = 0;
  }
}


void EcritureCarteSD(double Tab[TAILLE_TABLEAU]) {
  donnee = SD.open("DONNEE/Data.txt", FILE_WRITE);

  //ecriture des mesures
  for (int i = 0; i < 5; i++) {
    donnee.print(Tab[i]);
    donnee.print(",");
  }

  //ecriture de la date
  donnee.print(lround(Tab[5])); donnee.print("-");
  donnee.print(lround(Tab[6])); donnee.print("-");
  donnee.print(lround(Tab[7])); donnee.print(" ");
  donnee.print(lround(Tab[8])); donnee.print(":");
  donnee.print(lround(Tab[9])); donnee.print(":");
  donnee.print(lround(Tab[10]));
  donnee.println("");
  donnee.close();
}


void EnvoieBluetooth(double tab[TAILLE_TABLEAU]) {
  float a, b, c;
  a = tab[3]; b = tab[4]; c=tab[0];
  Serial.print(a);-
  Serial.print(";");
  Serial.print(b);
  Serial.print(";");
  Serial.print(c);
  
  Serial.print(",");
}


// ----------------------------------------------------------------------------------------------------------------------
// ------------- Début Programme ----------------------------------------------------------------------------------------
// ----------------------------------------------------------------------------------------------------------------------


void setup() {

  
 // ------------ Initialisation du port série et du capteur bmp280 ------------------------------------------------------
 
  Serial.begin(9600);
  
  if (!bmp280.begin()) {Serial.println("failed to initialised bmp");}
  bmp280.setTimeStandby(TIME_STANDBY_2000MS);     // Set the standby time to 2 seconds
  bmp280.startNormalConversion();  
    
  if (!ads.begin()) {
    Serial.println("Failed to initialize ADS.");
    while (!ads.begin());
  }

// ------------ Préparation du fichier de mesure sur la carte SD --------------------------------------------------------

  while (!SD.begin());
  Serial.print("carte SD OK");
  if (!SD.exists(DATA_DIR)) {
    SD.mkdir(DATA_DIR);
    donnee = SD.open("DONNEE/Data.txt", FILE_WRITE);
    donnee.println("Temp,press,alti,CO,CO2,date");
    donnee.close();
  }
}

void loop() {


// ------------ Vérification de la présence d'une carte SD --------------------------------------------------------------

  while (!SD.begin());
  

// ------------ Acquisition des mesures dans un tableau TabMesure -------------------------------------------------------

  bmp280.getCurrentMeasurements(temperature, pressure, altitude);  
  RTC.readTime();

 
  InitialiserTabMesure(Tab_Mesure);

  Tab_Mesure[0] = temperature;
  Tab_Mesure[1] = pressure;
  Tab_Mesure[2] = altitude;
  Tab_Mesure[3] = ConcentrationCO();
  Tab_Mesure[4] = ConcentrationCO2();
  Tab_Mesure[5] = RTC.yyyy;
  Tab_Mesure[6] = RTC.mm;
  Tab_Mesure[7] = RTC.dd;
  Tab_Mesure[8] = RTC.h;
  Tab_Mesure[9] = RTC.m;
  Tab_Mesure[10] = RTC.s;


// ----------- Sauvegarde des Mesures dans la carte SD et transmissions des données par Bluetooth -------------------------

  EcritureCarteSD(Tab_Mesure);
  EnvoieBluetooth(Tab_Mesure);
  delay(PERIODE_ECHANTILLONAGE);

}

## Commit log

2021-07-06 fichier gerber
    [circuitPanneauCarbOnFire-Edge_Cuts.gm1, circuitPanneauCarbOnFire-F_Cu.gtl, circuitPanneauCarbOnFire-F_Mask.gts, circuitPanneauCarbOnFire-F_SilkS.gto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]
2021-07-08 circuit electrique grove+capteur+panneauAvant
    [circuitPanneauCarbOnFire-Edge_Cuts.gm1, circuitPanneauCarbOnFire-F_Cu.gtl, circuitPanneauCarbOnFire-F_Mask.gts, circuitPanneauCarbOnFire-F_SilkS.gto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]
2021-07-16 ajout de fonction d'acquisition de mesure
2021-07-19 vérification avant impression
    [circuitPanneauCarbOnFire.kicad_pcb]
2021-07-19 renommage de dossier + ajout fiche technique
    [circuitPanneauCarbOnFire.kicad_pcb, circuitPanneauCarbOnFire.sch]
2021-07-20 pin analog read
2021-07-22 ajout data étallonage + avancement fiche technique
    [circuitPanneauCarbOnFire.sch]
2021-07-22 init courbe des résultats
    [courbe de résultats.ods]
2021-07-27 script python + pcb
2021-07-27 pcb + script python
    [circuitPanneauCarbOnFire.kicad_pcb, circuitPanneauCarbOnFire.sch]
2021-07-27 pcb+script python
2021-07-28 init analyse des résultats 22/07/21
    [courbe de résultats.ods]
2021-07-28 ajout de commentaire
2021-07-28 avancement fiche technique programme arduino
2021-08-04 init gestion de projet
2021-08-05 journal de bord 05/08
2021-08-17 changement de repertoire python
2021-08-27 renmmage des dossier
    [cloison horizontale.FCStd, plan_boitier.FCStd, support cloison.FCStd]
2021-09-09 ajout de commentaires
